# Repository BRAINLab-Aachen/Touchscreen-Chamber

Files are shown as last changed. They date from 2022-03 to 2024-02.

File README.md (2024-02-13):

# Touchscreen-Chamber

This repository contains information about a open-source touchscreen chamber for operant conditioning. 
Here, we want to share all relevant information about the touchscreen chamber used in the publication "A flexible python-based touchscreen chamber for operant conditioning reveals improved visual perception of cardinal orientations in mice" by Wiesbrock et al. 2022 (Link). 

Parts of the scripts are based on the Psychopy-Toolkit by Jonathan Peirce (https://www.psychopy.org/)

# Overview

Operant conditioning is crucial technique to quantatitate the perception of animals. We propose this touchscreen chamber to support open science and reproducibility. 
The scripts can be adapted to different experimental situations. For now, we propose pretraining procedures, so the animals can familarize themselves with the touchscreen chamber. Then there are three different approaches presented: Visual discrimination between different orientateted sine-wave gratings, a newly developed parallel visual discrimination test and, also new in the field of the mouse visual system, a staircase procedure with an adapting level of difficulty. 

# Requirements

|Part|Price|
|---|---|
|Measurement Computing 1208LS (Measurement Computing GmbH) | 125 €|
|Magnet ventile (SMC Pneumatik, 9900001809231)|50 €|
|PVC plates| 30 € |
|Display 11 inch (ELO touch 1002L)| 70 €|
|Infrared Frame (NJY touch, Guangdong, China)| 115 €|
|Clipper Box (Bauhaus)| 12 €|
|Logitech Z120 Speaker (Conrad Electronics)|17 €|
|Laptop| 210 €|
|Relais| 2 €|
|Cables, screws, tubes, piezo (Conrad electronics)|15 €|
|Webcam (Logitech C920)| 25 €|
|Dynavox TC-750 Amplifier| 28 €|
|Sum:| 699| 

# Assembly of the Hardware

First of all, the basis framework of the touchscreen chamber is needed (see https://github.com/BRAINLab-Aachen/Touchscreen-Chamber/blob/master/3d/TC.stl). We suggest to build it from single PVC plates assmebled with screws. The display holder needs to be two-parted according to the specific dimensions of the display and the infrared frame. The backside needs a fitting socket for the display and all cables as well as for the infrared frame. The frontside fixates the components and needs a hole, so the screen is visible. Note that the screenholder must not touch the glass of the infrared frame. On the opposite side of the screenholder, a hole needs to be drilled for the water spout in a height of 2 cm. The diameter of the hole should allow some minor movement of the water spout to get a stronger signal at the Piezo element. Above, a second hole is needed for a green LED light. The LED light (under consideration of specific resistances) needs to be connected to the DAQ's digital port.

The lick detection consists of a water spout, a piezo element, an amplifier (we used Dynavox TC-750 Amplifier) and a DAQ (Measurement Computing 1208LS (Measurement Computing GmbH) ). The water spout should be long enough to attach the piezo element to it outside the basic framework. According to the specific piezo elements used, it needs to be connected to the amplifier input. The amplifier output is connected to the analog ports of the DAQ. Using the software, delivered with the DAQ it should be tested, if it is visible, when the piezo element is moved. 

The water delivery system consists of a magnet ventile, a relais and the DAQ. The digital port of the DAQ needs to be connected to the relais, while the relais is connected to power and the magnet ventile. By getting the signal from the digital port, the cirquit is closed and the magnet ventile opens. A water tank (we use 10 ml syringes without a cannula) needs to be connected with a fitting tube to the intake side of the ventile. The water spout needs to be connected via a tube to the outtake side of the ventile. Important: Please take the specifications of single parts into consideration. Magnet ventiles and relais from different vendors can have a large variability in terms of power and voltage. 

The dimensions of the basis framework fits into a larger variety of clipper boxes. This is the "basic" solution. If you are running experiments, which needs a higher level of silence while they are in a not-so-quite environment, please consider the use of a proper sound attenuation box. 

## Installation ##
1. In this Project an ESP32 with a CP2102 chip is used. This requires the installation of the appropriate USB-drive:
"https://www.silabs.com/developers/usb-to-uart-bridge-vcp-drivers?tab=downloads"

2. Futher the Arduino IDE is required to upload the code to the ESP32:
"https://www.arduino.cc/en/software"

3. The ESP32 Board need to be added to Arduino IDE. See instructions here: "https://randomnerdtutorials.com/installing-the-esp32-board-in-arduino-ide-windows-instructions/"
In short: Go to "File>Preferences", then add "https://raw.githubusercontent.com/espressif/arduino-esp32/gh-pages/package_esp32_index.json" under “Additional Board Manager URLs”

# Software

At the moment the Touchscreen Chamber is running with Python 2.7. Since not everyone is using Python2, we suggest the following to create a dedicated environment:

conda create --name TouchscreenChamber Python==2.7
pip install Psychopy==1.83.04

For the installation one more package is needed. First of all for the control of the DAQ via Python the Package UniversalLibrary is needed, which can be found here: https://pypi.org/project/PyUniversalLibrary/#files or pip install mcculw

To prepare your experiments, you need to start piezo calibration.py first. This script reads the signal from the piezo element. According to the specific model of your piezo element, a daily calibration is probably needed. The threshold for a touch at the lick detection needs to be adapted in following experimental scripts.

The pretraining consists of two scripts. For autoreward.py, the screen can be deactivated. In this phase, the green led light is activated, when a reward is available. After the mouse collected the reward, the green light turns off and turns on again after a predefined timeout. After 2-3 sessions, the mouse should have collected at least one reward per minute and can proceed to the next stage. The next step is the touch training (touchtraining.py), where the animal learns to touch the screen in order to get a reward. Again, it turns out to be benefitial, when the mice are able to complete one trial per minute on two consecutive sessions. 

Congratulations! Your mouse is ready for an operant conditioning experiment. We propose different orientation discrimination tasks (staircase, visual discrimination and parallel visual discrimination learning). Using the built-in GUI of Psychopy, it is also possible to create a large variety of different tasks and use it in the touchscreen chamber. The specific functions can be taken from the orientation discrimination tasks.

# Future

Stay tuned for the Python 3 upgrade and Arduino support in the future.

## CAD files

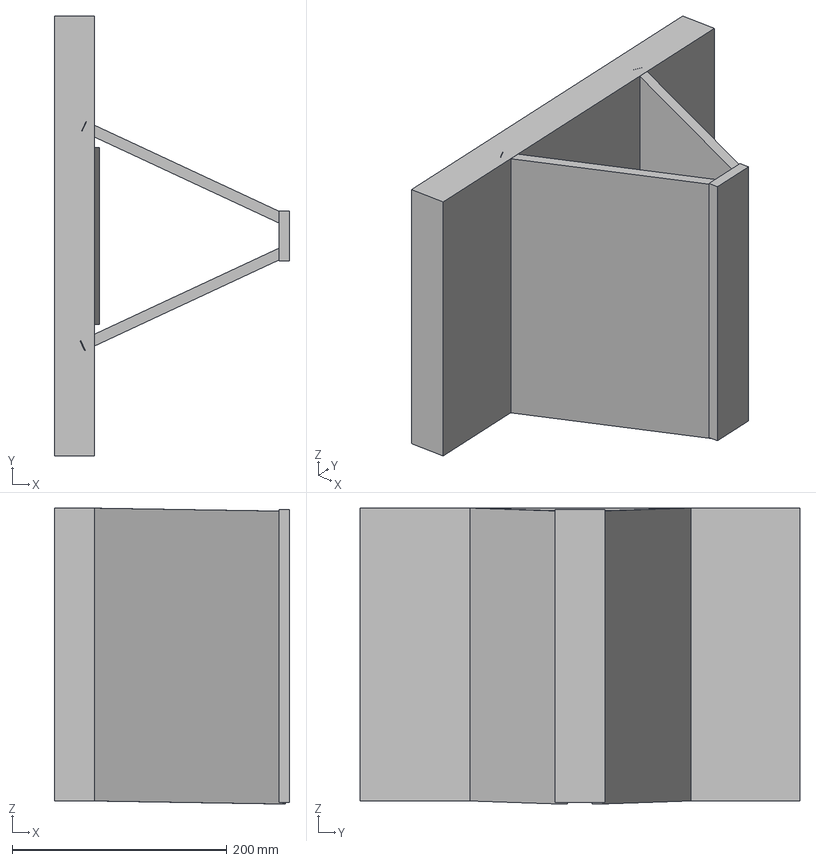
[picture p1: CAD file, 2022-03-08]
3d/TC.3mf
219.5 x 410.0 x 276.0 mm

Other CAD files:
3d/TC.obj
3d/TC.stl

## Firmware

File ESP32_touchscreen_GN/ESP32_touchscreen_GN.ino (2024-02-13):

#include "Arduino.h"
#include "LickDetection.h"
#include "TimedDigitalPulse.h"
#include "SerialSend.h"

////////////////////////////////////////////////////
// LickDetection ///////////////////////////////////
////////////////////////////////////////////////////
// Inputs for lick sensors
#define SPOUTSENSOR 13 // touch line for left spout

// Init LickDetection
LickDetection lick(SPOUTSENSOR);
LickDetection* lick_ptr = &lick;


////////////////////////////////////////////////////
// Experiment //////////////////////////////////////
////////////////////////////////////////////////////
// PINs to control Setup
#define PIN_VALVE 12 // Water valve connected to an optocoupler
#define LED_PIN 14 // LED

SerialSend RespondedSerialObject;
TimedDigitalPulse VALVE;

////////////////////////////////////////////////////
// USB Serial Communication ////////////////////////
////////////////////////////////////////////////////
#define FirmwareVersion "0001" // Version Nr. returned upon request
#define moduleName "HomecageTouchscreenESP32" // Module name used to identify desired Serial device

// Byte codes for serial communication
// inputs
#define ADJUST_TOUCHLEVEL 75 // identifier to re-adjust threshold for touch sensors. Will sample over 1 second of data to infer mean/std of measurements.

#define FLUSH_VALVE 100 // flush valves outside of the experiment using this command
#define LED_ON 101
#define LED_OFF 102
#define WAIT_FOR_LICK_REWARDED 103
#define WAIT_FOR_LICK_NOT_REWARDED 104
#define MODULE_INFO 255  // returns module information

#define GOT_BYTE 14 // positive handshake for Serial commands
#define DID_ABORT 15 // negative handshake for Serial commands

// Serial COM variables
unsigned long serialClocker = millis();
int FSMheader = 0;
bool midRead = false;
bool read_msg_length = false;
float temp[22]; // temporary variable for general purposes

unsigned long lickClocker = millis();

unsigned long open_duration = 75070;  // in us

//////////////////////////////////////////////////////////////////////////////////////////////////////////////////////////////////////////////////////////////////////////
void setup() {
  Serial.begin(9600);

  pinMode(LED_PIN, OUTPUT);
  VALVE.configure(PIN_VALVE, open_duration);

  RespondedSerialObject.configure(FLUSH_VALVE);
}

void loop() {
  ReadSerialCommunication();
  lick_ptr->ReadTouchSensors();

  VALVE.update();
  RespondedSerialObject.update();
} // end of void loop


// Functions:
void ReadSerialCommunication() {
  // Serial Communication over USB
  // Main purpose is to start a new trial
  if (Serial.available() > 0) {
    if (!midRead) {
      FSMheader = Serial.read();
      midRead = 1; // flag for current reading of serial information
      serialClocker = millis(); // counter to make sure that all serial information arrives within a reasonable time frame (currently 100ms)
      read_msg_length = false;
    }
    if (midRead) {
      if (FSMheader == FLUSH_VALVE) {
        if (Serial.available() > 1) {
          // I have to call FLUSH_VALVE once at the beginning of the session to set the desired Valve open duration from
          // the calibration. This is not necessarily intuitive, for readability I might want to make those two separate commands.
          unsigned long open_duration = readSerialChar(Serial.read());
          Serial.write(GOT_BYTE); midRead = 0;
          VALVE.change_duration(open_duration);
          VALVE.sendTrigger();
          midRead = 0;
        }
      }
      else if (FSMheader == ADJUST_TOUCHLEVEL) { // check mean and std for all touch lines to adjust thresholds
        if (Serial.available() > 1) {
          lick.command_AdjustTouchLevel(readSerialChar(Serial.read()));
          Serial.write(GOT_BYTE); midRead = 0;
        }
        else if ((millis() - serialClocker) >= 100) {
          Serial.write(DID_ABORT); midRead = 0;
        }
      }
      else if (FSMheader == LED_ON) {
        Serial.write(GOT_BYTE); midRead = 0;
        digitalWrite(LED_PIN, HIGH);
        midRead = 0;
      }
      else if (FSMheader == LED_OFF) {
        Serial.write(GOT_BYTE); midRead = 0;
        digitalWrite(LED_PIN, LOW);
        midRead = 0;
      }
      else if (FSMheader == WAIT_FOR_LICK_REWARDED) {
        if (Serial.available() > 1) {
          unsigned long duration = readSerialChar(Serial.read());
          Serial.write(GOT_BYTE); midRead = 0;

          lickClocker = millis();
          while (millis() - lickClocker < duration) {
            // Monitor for Licks. Note this is blocking! It hasn't been an issue, as the Microcontroller doesn't have anything else to do right now but rethink this if it ever changes.
            lick_ptr->ReadTouchSensors();
  
            if (lick_ptr->spoutTouch) {
              VALVE.sendTrigger();
              RespondedSerialObject.send();
              break;
            }
          }
          digitalWrite(LED_PIN, LOW);
          midRead = 0;
        }
        else if ((millis() - serialClocker) >= 100) {
          Serial.write(DID_ABORT); midRead = 0;
        }
      }
      else if (FSMheader == WAIT_FOR_LICK_NOT_REWARDED) {
        if (Serial.available() > 1) {
          // There isn't really a need to send a duration here as well. Consider removing unless this makes is simpler from the PC side
          unsigned long duration = readSerialChar(Serial.read());
          Serial.write(GOT_BYTE); midRead = 0;
  
          lickClocker = millis();
          while (millis() - lickClocker < duration) {          
            lick_ptr->ReadTouchSensors();
  
            if (lick_ptr->spoutTouch) {
              RespondedSerialObject.send();
              break;
            }
          }
          digitalWrite(LED_PIN, LOW);
          midRead = 0;
        }
        else if ((millis() - serialClocker) >= 100) {
          Serial.write(DID_ABORT); midRead = 0;
        }
      }
      else if (FSMheader == MODULE_INFO) { // return module information
        returnModuleInfo();
        midRead = 0;
      }

      
  
      else if (FSMheader == GOT_BYTE){
        // The Serial COM waiting for confirmation inside Experiment makes Issues.
        // This is not elegant, but I'm assuming now that any GOT_BYTE received here is in response to the Stimulus/Response signals send inside Experiment
        RespondedSerialObject.waiting_for_confirmation = false;
        //Serial.write(69);
        midRead = 0;
      }
      else {
        //flush the Serial to be ready for new data
        while (Serial.available() > 0) {
          Serial.read();
        }
        midRead = 0;
  
  //      //send abort to request resend
  //      Serial.write(DID_ABORT); midRead = 0;
      }
    }
  }

  if (midRead && ((millis() - serialClocker) >= 100)) {
      //flush the Serial to be ready for new data
      while (Serial.available() > 0) {
        Serial.read();
      }

      //send abort to request resend
      Serial.write(DID_ABORT); midRead = 0;
  }
}

float readSerialChar(byte currentRead){
  float currentVar = 0;
  byte cBytes[currentRead-1]; // current byte
  int preDot = currentRead; // indicates how many characters there are before a dot
  int cnt = 0; // character counter

  if (currentRead == 1){
    currentVar = Serial.read() -'0'; 
  }

  else {
    for (int i = 0; i < currentRead; i++) {
      cBytes[i] = Serial.read(); // go through all characters and check for dot or non-numeric characters
      if (cBytes[i] == '.') {cBytes[i] = '0'; preDot = i;}
      if (cBytes[i] < '0') {cBytes[i] = '0';}
      if (cBytes[i] > '9') {cBytes[i] = '9';}
    }
  
    // go through all characters to create new number
    if (currentRead > 1) {
      for (int i = preDot-1; i >= 1; i--) {
        currentVar = currentVar + ((cBytes[cnt]-'0') * pow(10,i));
        cnt++;
      }
    }
    currentVar = currentVar + (cBytes[cnt] -'0'); 
    cnt++;
  
    // add numbers after the dot
    if (preDot != currentRead){
      for (int i = 0; i < (currentRead-preDot); i++) {
        currentVar = currentVar + ((cBytes[cnt]-'0') / pow(10,i));
        cnt++;
      }
    }
  }
  return currentVar;
}

void returnModuleInfo() {
  Serial.write(65); // Acknowledge
  Serial.write(FirmwareVersion); // 4-byte firmware version
  Serial.write(sizeof(moduleName)-1); // Length of module name
  Serial.print(moduleName); // Module name
  Serial.write(0); // 1 if more info follows, 0 if not
}

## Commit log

2022-08-02 Add files via upload
    Added Example Datasets and Analysis scripts
    [01_1218_untitled.py_2019_Feb_06_1146.csv, 02_1218_untitled.py_2019_Feb_07_1108.csv, 02_293_untitled.py_2018_Feb_14_1555.csv, 03_1218_untitled.py_2019_Feb_08_14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]
2024-01-22 Updated codes for the ESP32
    Those are the functions that control the ESP32. They are integrated into the general routines in Touchscreen-Chamber-Gerion. Now that there are copies of those routines in "Preparation", "Parallel Vi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
    I think the ideal structure of this Repo should be a single function that realized the entire setup and task (using those individual general module functions) and is only called with different settin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
2024-01-22 Update README.md
    Added the Installation steps needed to use the ESP32
